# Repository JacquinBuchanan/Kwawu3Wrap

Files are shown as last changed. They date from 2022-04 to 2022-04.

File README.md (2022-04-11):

# Kwawu Arm 3.0 - Wrap Version
This is functional 3D printable device for those with forearm limb differences. It has better functionality and easier to assemble than the 2.0 version.

!!!! DO NOT PRINT THESE STL FILES DIRECTLY. !!!!!
Download all the files and use the OpenSCAD to modify and scale the STL files.

The included PDF file "Kwawu 3.0 Wrap Version Instructional Guide" will show you how to download the Open SCAD program and use the code in these files to size this model.

Instructional videos for this design can be found here.
https://www.youtube.com/playlist?list=PLO2iVws0boe0Yrh_1auXd5TTmXr6_y3zT

I have redesigned the Kwawu arm to be more natural looking and more functional. The terminal device has a much higher grip strength and functionality. Very good at picking up small things with index finger and thumb and big things with whole hand.

This version is the wrap version intended for people with long forearm residual limbs.
There is a socket version for people with short forearm residuals

I would like to thank the e-NABLE community. It is a wonderful group to be a part of.

To get involved with the e-NABLE community please visit https://hub.e-nable.org

Shield: [][cc-by]

This work is licensed under a
[Creative Commons Attribution 4.0 International License][cc-by].

[][cc-by]

[cc-by]: http://creativecommons.org/licenses/by/4.0/
[cc-by-image]: https://i.creativecommons.org/l/by/4.0/88x31.png
[cc-by-shield]: https://img.shields.io/badge/License-CC%20BY%204.0-lightgrey.svg

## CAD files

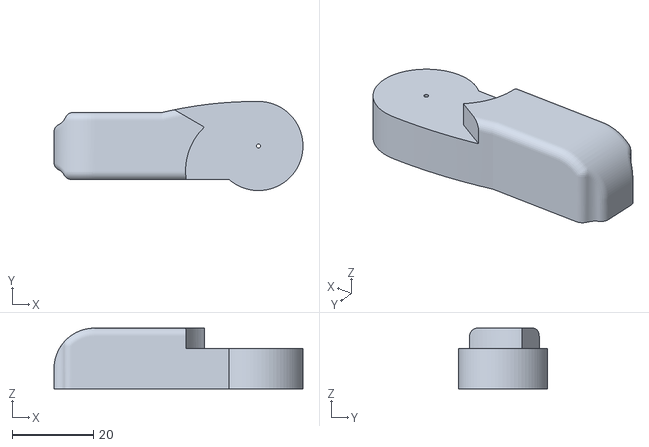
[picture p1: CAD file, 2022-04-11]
o_Arm2.stl
61.4 x 22.0 x 15.0

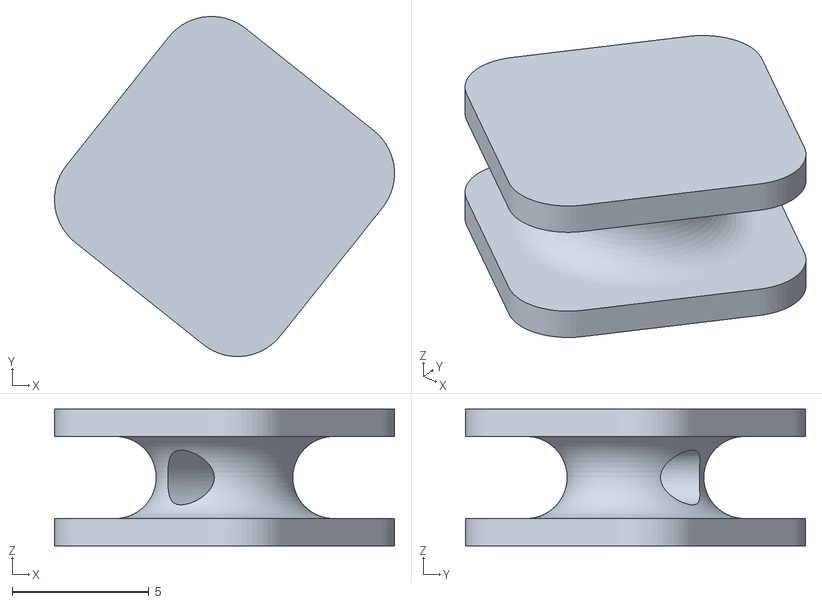
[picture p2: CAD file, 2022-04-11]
o_Tensioner.stl
12.4 x 12.4 x 5.00

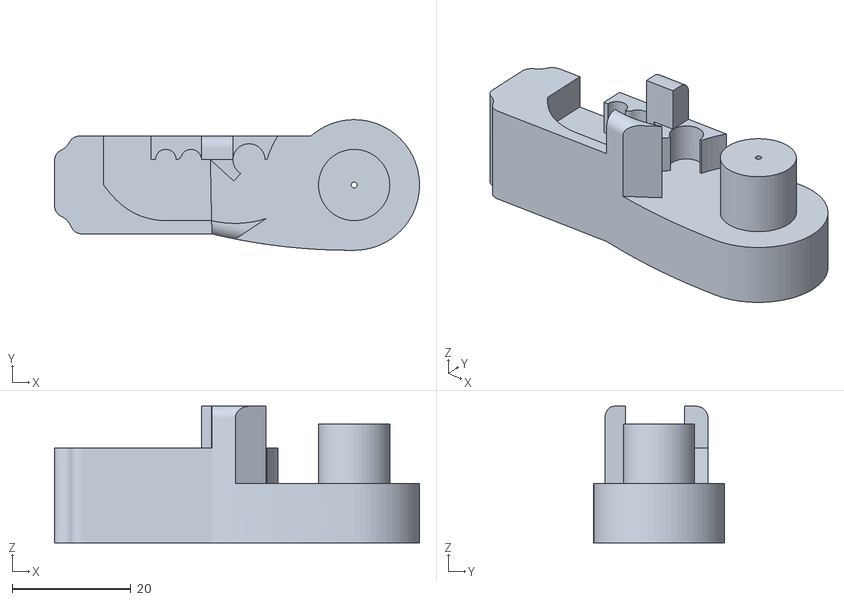
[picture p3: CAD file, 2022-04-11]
o_Arm1.stl
61.4 x 22.0 x 23.0

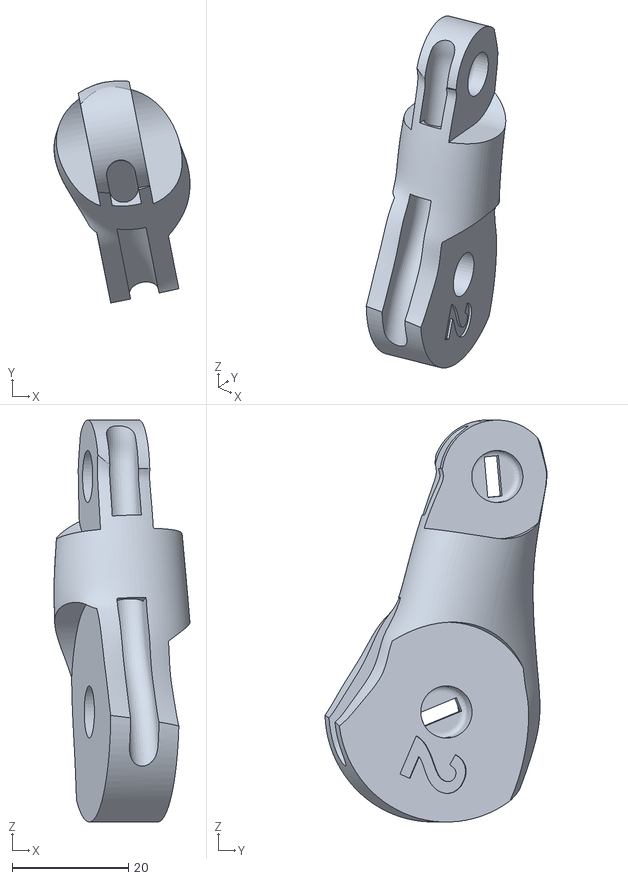
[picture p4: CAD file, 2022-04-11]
o_IndexFingerPhalanx.stl
23.4 x 38.3 x 69.3

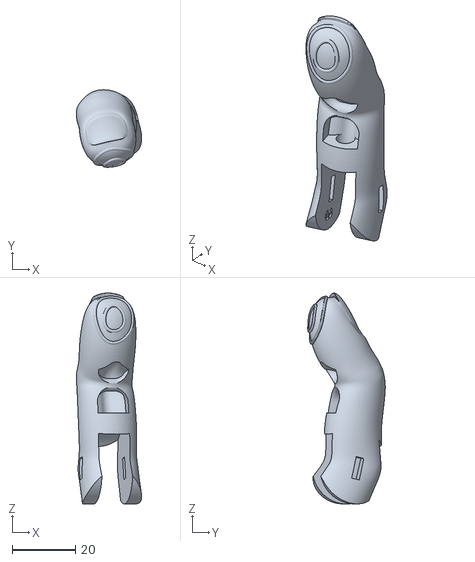
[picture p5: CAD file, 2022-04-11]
o_MiddleFingerEnd.stl
20.6 x 24.5 x 66.6

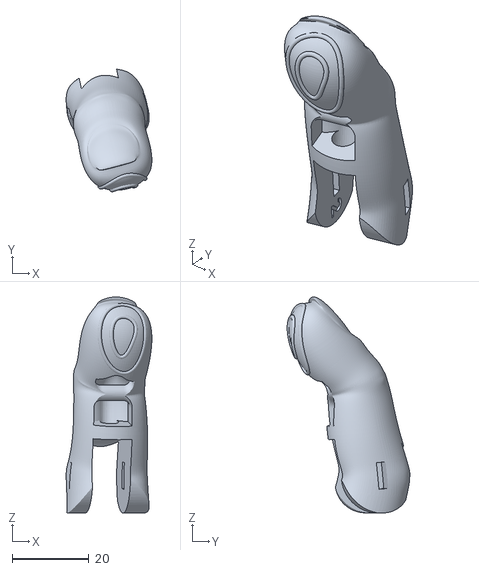
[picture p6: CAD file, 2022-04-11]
o_IndexFingerEnd.stl
22.3 x 31.9 x 56.2

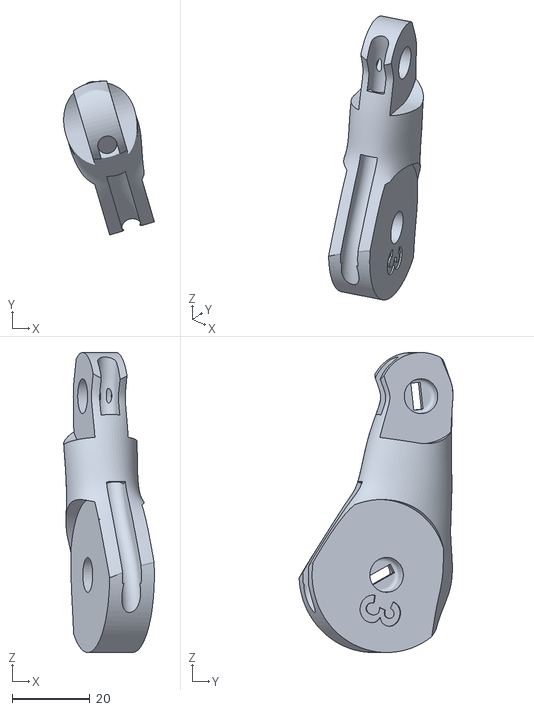
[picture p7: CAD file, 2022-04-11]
o_MiddleFingerPhalanx.stl
23.4 x 39.6 x 77.3

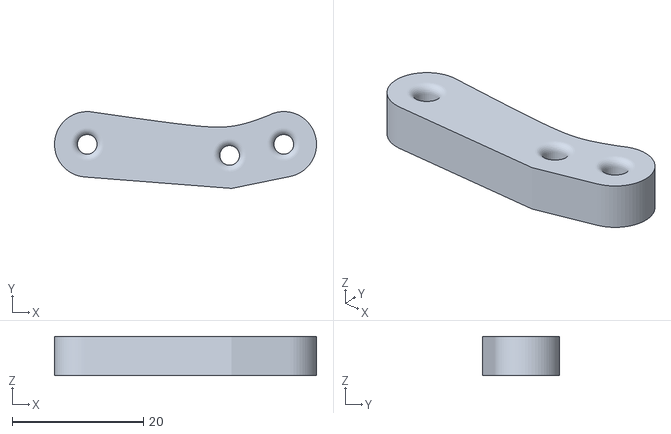
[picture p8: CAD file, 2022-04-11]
o_WhippleTreeSecondary.stl
40.0 x 11.7 x 6.00

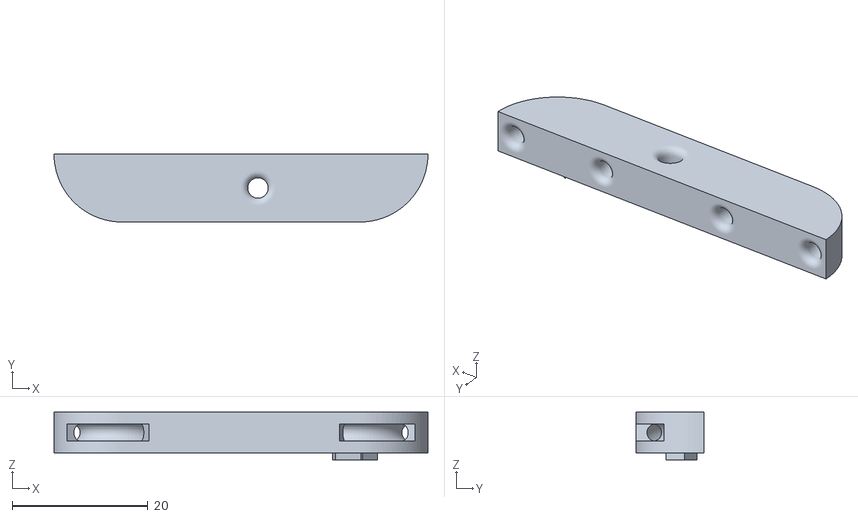
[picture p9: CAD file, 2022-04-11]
o_WhippleTreePrimary.stl
55.0 x 10.0 x 7.00

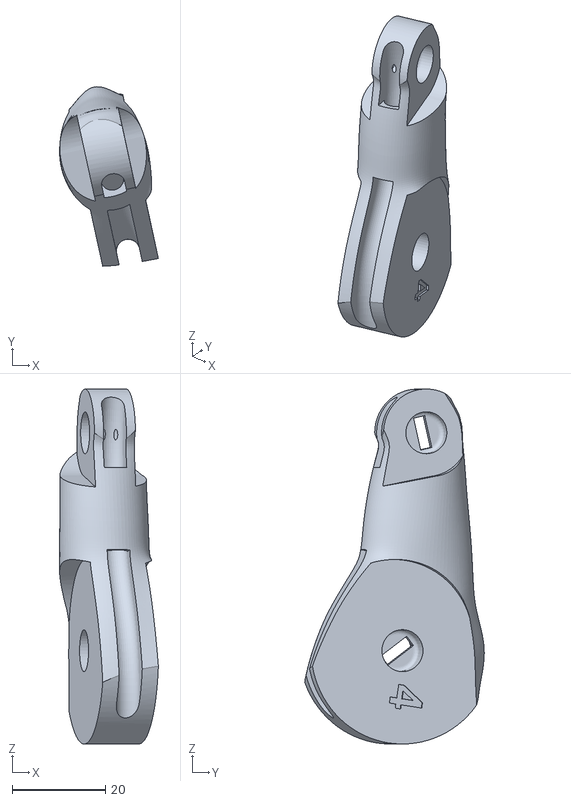
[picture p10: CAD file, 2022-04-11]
o_RingFingerPhalanx.stl
21.1 x 38.5 x 76.1

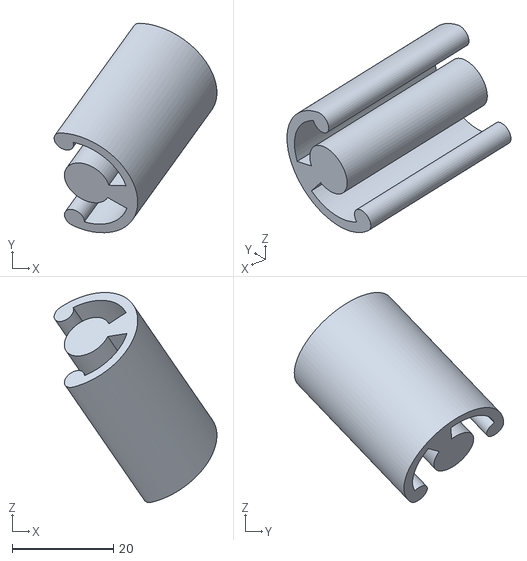
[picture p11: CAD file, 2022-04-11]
o_PencilHolderTool.stl
32.1 x 41.3 x 41.4

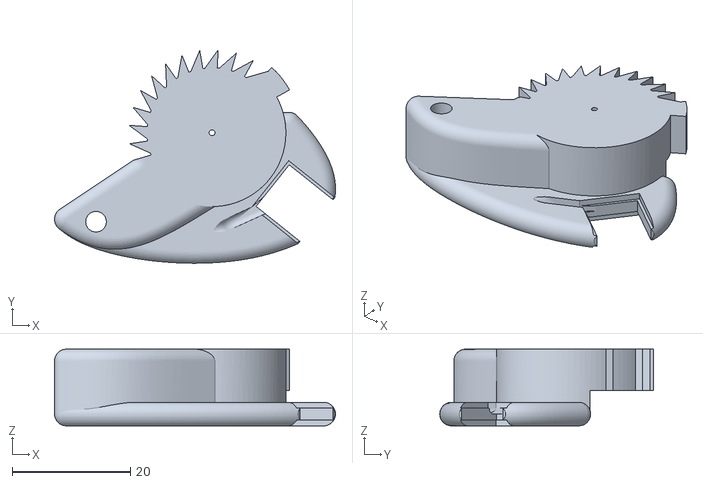
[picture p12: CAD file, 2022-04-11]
o_Ratchet.stl
47.6 x 36.2 x 13.0

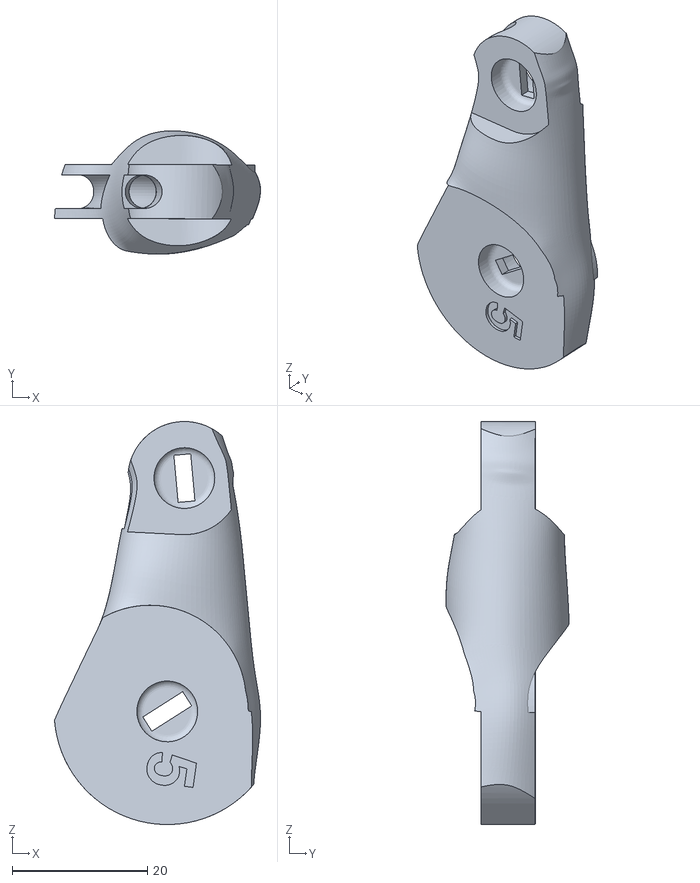
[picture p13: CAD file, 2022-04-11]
o_PinkyFingerPhalanx.stl
30.5 x 18.3 x 59.7

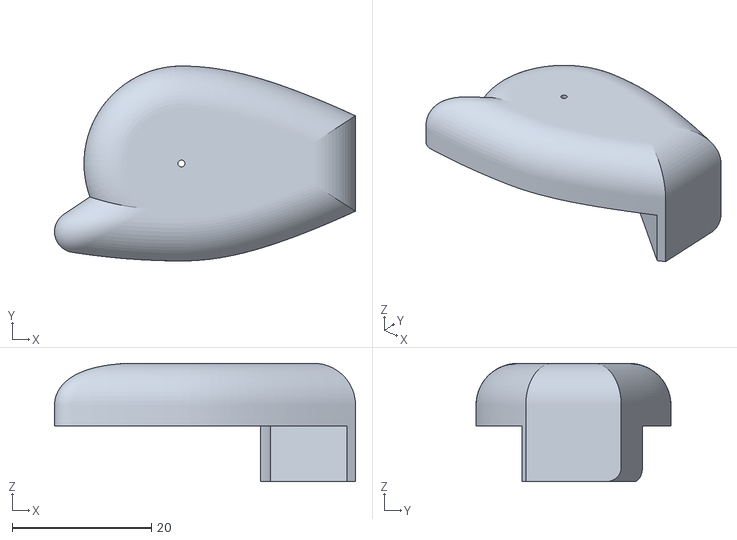
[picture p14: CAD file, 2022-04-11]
o_Cuff1.stl
43.2 x 28.0 x 17.0

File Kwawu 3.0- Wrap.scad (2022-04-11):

// The Kwawu 3.0 prosthetic Arm - Wrap Version
// By Jacqun Buchanan
// Parameteric 3-d printable prosthetic arm
//
// This design is licensed under the Creative Commons - Attribution - Share Alike license.

// The ISO thread code is by Trevor Moseley

// Choose Part
Part = "Cuff1"; // [Palm,PalmTop,WristButton,WristCover, Cuff1,Cuff2,Cuff3,CuffLeatherTemplate,UpperArm1,LowerArm1,UpperArm2,LowerArm2,UpperArm3, LowerArm3, UpperArmLeatherTemplate, LowerArmLeatherTemplate, Ratchet, Latch, LatchCover, WristAttachment, WristBolt, PalmBolt, WristBoltPin, ElbowBolt1,ElbowBolt2,IndexFingerEnd, IndexFingerPhalanx, MiddleFingerEnd, MiddleFingerPhalanx, PinkyFingerEnd, PinkyFingerPhalanx, RingFingerEnd, RingFingerPhalanx, ThumbEnd, ThumbPhalanx, Tensioner, WhippleTreePrimary, WhippleTreeSecondary,PencilHolderCover, Hinges]
//Left or Right Arm
LeftRight = "Right"; //[Right, Left]
//Wraps are made from leather or plastic
LeatherOrPlastic = "Leather"; //[Leather, Plastic]
// Across all four knuckles (mm)
HandWidth = 96; //[65:186]
// Elbow crease to wrist attachment (mm)
ArmLength = 282; //[141: 564]
// Circumference of Forearm just below elbow crease (mm)
ForearmCircumference = 270; //[135: 542]
// - Circumference of Bicep (mm)
BicepCircumference = 294; //[147: 600]
// Padding Thickness -inside forearm and cuff (mm)
PaddingThickness = 2; //[0: 10]
// ISO metric bolt holding palm together (mm) 
PalmBoltDiameter = 6;//[4, 6, 8]
// ISO metric bolt holding cuff and arm together (mm)
ElbowBoltDiameter = 8; //[4, 6, 8, 10, 12, 14]
// Diameter of leather rivet shaft (mm)
RivetShaftDiameter = 5; //[2.4, 2.8, 3.1, 4, 5, 6]
// Velcro strap width (mm)
StrapWidth = 25;//[10: 60]
// Include Pencil Holder
PencilHolder = "No"; // [Yes,No]
/* [Hidden] */


SlotSize = 0.5;
SlotLength = 10;//length of the opening slot
SlotSpacing = 3;//spacing between slots
SlotWidth = 2.4;//width of slots 
//The thickness of the cuff
ShellThickness = 2;

// This is an amount added to the pencil cover length. 
// When this is zero the pencil cover is as tight as possible.
// Make it larger to fit around larger/thicker pencils
PencilCoverAddedLength = 4.0;

PI =  3.141592653589793238;
HandVersion = "V3.0";

HandScale = HandWidth / 96;
WristCircumference = HandScale * 169;
WristCircumferenceWPadding = ((WristCircumference/PI) + 2*PaddingThickness  - 2*ShellThickness)*PI;
ForearmCircumferenceWPadding = ((ForearmCircumference/PI) + 2*PaddingThickness)*PI;
ForeArmCircumferenceScale = ForearmCircumferenceWPadding/270;
ElbowPartsScale = max(0.73, ForeArmCircumferenceScale);
ForearmDiameterWPadding = ForearmCircumferenceWPadding/PI;
BicepCircumferenceWPadding = ((BicepCircumference/PI) + 2*PaddingThickness)*PI;
BicepDiameterWPadding = BicepCircumferenceWPadding/PI;
CuffScale = BicepCircumferenceWPadding/270;
CuffLength = CuffScale * 90;


WristBoltDia = 18;
$fn=30;

if(Part == "Cuff1") {
    if (LeftRight == "Left") {
        mirror([1,0,0]) MakeCuff1();
    }else {
        MakeCuff1();
    }
}

if(Part == "Cuff2") {
    if (LeftRight == "Left") {
        mirror([1,0,0]) MakeCuff2();
    } else {
        MakeCuff2();
    }
}

if(Part == "Cuff3") {
    if (LeftRight == "Left") {
        mirror([1,0,0]) MakeCuff3();
    } else {
        MakeCuff3();
    }
}

if(Part== "CuffLeatherTemplate")
    {
    if (LeftRight == "Left") {
        mirror([1,0,0]) MakeCuffLeatherTemplate();
    } else {
        MakeCuffLeatherTemplate();
    }
}

if(Part == "UpperArm1") {
    if (LeftRight == "Left") {
        mirror([1,0,0]) MakeUpperArm1();
    } else {
         MakeUpperArm1();
    }
}

if(Part == "LowerArm1") {
    if (LeftRight == "Left") {
        mirror([1,0,0]) MakeLowerArm1();
    } else {
        MakeLowerArm1();
    }
}

if(Part == "UpperArm2") {
    if (LeftRight == "Left") {
        mirror([1,0,0]) MakeUpperArm2();
    } else {
        MakeUpperArm2();
    }
}

if(Part == "LowerArm2") {
    if (LeftRight == "Left") {
        mirror([1,0,0]) MakeLowerArm2();
    } else {
        MakeLowerArm2();
    }
}


if(Part == "UpperArm3") {
    if (LeftRight == "Left") {
        mirror([1,0,0]) MakeUpperArm3();
    } else {
        MakeUpperArm3();
    }
}

if(Part == "LowerArm3") {
    if (LeftRight == "Left") {
        mirror([1,0,0]) MakeLowerArm3();
    } else {
        MakeLowerArm3();
    }
}

if(Part == "UpperArmLeatherTemplate") {
    if (LeftRight == "Left") {
        mirror([1,0,0]) MakeUpperArmLeatherTemplate();
    } else {
        MakeUpperArmLeatherTemplate();
    }
}

if(Part == "LowerArmLeatherTemplate") {
    if (LeftRight == "Left") {
        mirror([1,0,0]) MakeLowerArmLeatherTemplate();
    } else {
        MakeLowerArmLeatherTemplate();
    }
}

if(Part == "Ratchet") {
    if (LeftRight == "Left") {
        mirror([1,0,0]) MakeRatchet();
    } else {
        MakeRatchet();
    }
}

if(Part == "Tensioner")
    MakeTensioner();

if(Part == "Latch") {
    if (LeftRight == "Left") {
        mirror([1,0,0]) MakeLatch();
    } else {
        MakeLatch();
    }
}

if(Part == "LatchCover") {
    if (LeftRight == "Left") {
        mirror([1,0,0])  MakeLatchCover();
    } else {
        MakeLatchCover();
    }
}

if(Part == "WristAttachment") {
    if (LeftRight == "Left") {
        mirror([1,0,0]) rotate(a=[180,0,0])MakeWristAttachment();
    } else {
        rotate(a=[180,0,0])MakeWristAttachment();
    }
}

if(Part == "WristBolt") {
    if (LeftRight == "Left") {
        mirror([1,0,0]) rotate(a=[180,0,0])MakeWristBolt();
    } else {
        rotate(a=[180,0,0])MakeWristBolt();
    }
}

if(Part == "WristBoltPin")
{
    rotate(a=[90,0,0])MakeWristBoltPin();
}

if(Part == "ElbowBolt1"){
    if (LeftRight == "Left") {
        mirror([1,0,0]) rotate(a=[180,0,0]) MakeElbowBolt(26);
    } else {
        rotate(a=[180,0,0]) MakeElbowBolt(26);
    }
}

if(Part == "ElbowBolt2"){
    if (LeftRight == "Left") {
        mirror([1,0,0]) rotate(a=[180,0,0]) MakeElbowBolt(19);
    } else {
        rotate(a=[180,0,0]) MakeElbowBolt(19);
    }
}

if(Part == "PalmBolt"){
    if (LeftRight == "Left") {
        mirror([1,0,0]) rotate(a=[180,0,0])MakePalmBolt();
    } else {
        rotate(a=[180,0,0])MakePalmBolt();
    }
}

if (Part == "Palm") {
    if (LeftRight == "Left") {
        mirror([1,0,0]) MakePalm();
    } else {
        MakePalm();
    }
}

if(Part =="WristButton")
{
    //Rotate just to orient for printing
    if (LeftRight == "Left") {
        mirror([1,0,0]) rotate(a=[180,0,0])MakeWristButton();
    } else {
    
        rotate(a=[180,0,0])MakeWristButton();
    }
    
}

if(Part =="WristCover")
{
    MakeWristCover();
    
}

if (Part == "PalmTop") {
    //Rotate just to orient for printing
    if (LeftRight == "Left") {
        mirror([1,0,0]) rotate(a=[90,7,]) MakePalmTop();
    } else {
        rotate(a=[90,7,0])MakePalmTop();
    }
}

if(Part == "IndexFingerEnd") {  
    if (LeftRight == "Left") {
        mirror([1,0,0]) IndexFingerEnd();
       } else {
        IndexFingerEnd();
    }
}

if(Part == "IndexFingerPhalanx") { 
     if (LeftRight == "Left") {
        mirror([1,0,0]) IndexFingerPhalanx();
       } else {
        IndexFingerPhalanx();
    }
}
        
if(Part == "MiddleFingerEnd") { 
     if (LeftRight == "Left") {
        mirror([1,0,0]) MiddleFingerEnd();
       } else {
        MiddleFingerEnd();
    }
}
            
if(Part == "MiddleFingerPhalanx") { 
     if (LeftRight == "Left") {
        mirror([1,0,0]) MiddleFingerPhalanx();
       } else {
        MiddleFingerPhalanx();
    }
}
                
if(Part == "PinkyFingerEnd") { 
     if (LeftRight == "Left") {
        mirror([1,0,0]) PinkyFingerEnd();
       } else {
        PinkyFingerEnd();
    }
}

if(Part == "PinkyFingerPhalanx") { 
     if (LeftRight == "Left") {
        mirror([1,0,0]) PinkyFingerPhalanx();
       } else {
        PinkyFingerPhalanx();
    }
}

if(Part == "RingFingerEnd") { 
     if (LeftRight == "Left") {
        mirror([1,0,0]) RingFingerEnd();
       } else {
        RingFingerEnd();
    }
}

if(Part == "RingFingerPhalanx") { 
     if (LeftRight == "Left") {
        mirror([1,0,0]) RingFingerPhalanx();
       } else {
        RingFingerPhalanx();
    }
}

if(Part == "ThumbEnd") { 
     if (LeftRight == "Left") {
        mirror([1,0,0]) ThumbEnd();
       } else {
        ThumbEnd();
    }
}

if(Part == "ThumbPhalanx") { 
     if (LeftRight == "Left") {
        mirror([1,0,0]) ThumbPhalanx();
       } else {
        ThumbPhalanx();
    }
}

if(Part == "WhippleTreePrimary") { 
     if (LeftRight == "Left") {
        mirror([1,0,0]) rotate(a=[180,0,0])WhippleTreePrimary();
       } else {
        rotate(a=[180,0,0])WhippleTreePrimary();
    }
}

if(Part == "WhippleTreeSecondary") { 
     if (LeftRight == "Left") {
        mirror([1,0,0]) WhippleTreeSecondary();
       } else {
        WhippleTreeSecondary();
    }
}

if(Part == "PencilHolderCover")
{
    PencilHolderCover();
}
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

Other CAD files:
o_ThumbEnd.stl
o_ThumbPhalanx.stl
o_LatchCover.stl
o_Palm.stl
Arm1.stl
o_Cuff2.stl
o_Latch.stl
o_PalmTop.stl
o_PinkyFingerEnd.stl
o_RingFingerEnd.stl

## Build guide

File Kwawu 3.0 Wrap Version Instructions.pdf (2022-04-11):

# Kwawu Arm 3.0 Wrap Version

# Instruction Guide

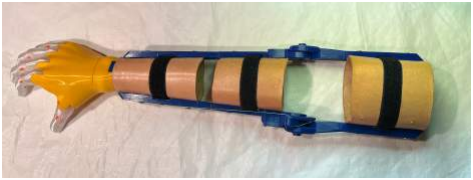
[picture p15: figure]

# Jacquin Buchanan January 2022

This work is licensed under the Creative Commons Attribution 4.0 International License. To view a copy of this license, visit https://creativecommons.org/licenses/by/4.0/ or send a letter to Creative Commons, PO Box 1866, Mountain View, CA 94042, USA.

In simple language you can:
- Share — copy and redistribute the material in any medium or format.
- Adapt — remix, transform, and build upon the material for any purpose, even commercially.
Under the following terms:
- Attribution — You must give appropriate credit, provide a link to the license, and indicate if changes were made. You may do so in any reasonable manner, but not in any way that suggests the licensor endorses you or your use.
- No additional restrictions — You may not apply legal terms or technological measures that legally restrict others from doing anything the license permits.

Kwawu Arm 3.0 Wrap Version 2

This instruction guide shows the steps and processes in making a Kwawu 3.0 transradial prosthetic arm and hand. This arm is best suited for a recipient with a residual forearm longer than half of the recipient’s intact forearm. See the Socket version of the Kwawu 3.0 for an arm better suited for a residual arm that is half or shorter than the recipient’s intact arm.

To complete the instructions in this document and fully prepare an arm for usage can take 30 to 40 hours of labor. Assuming most people reading this document are doing this project in their spare time, expect it to take several weeks. Likely the first one you make may not fit or work exactly right, when you try it on the recipient, so you will have to reprint a part and partially reassemble the arm. It is important to set this expectation for yourself and the person you are making the arm for. Explain to them and yourself that the whole process can take months.

Improvements of the Kwawu 3.0 over the Kwawu 2.0 device include:

- Easier stringing the fingers to hand mechanism
- Better response of elbow bend to finger squeeze
- A locking but adjustable wrist
- Improved latch mechanism to fix hand fingers in a grasped position
- The Cuff and Forearm have plastic or leather options
- Thermoforming is not required
- A redesigned tensioner
- Easier assembly
- Compatible with wider range of TPU ShoreA hardness

# Qualifying Expectations

This arm was designed by hobbyists in hopes that it would fill a need for someone who has had a congenital or traumatic amputation. We do not claim to be professional prosthetists and this arm is designed as an assistive device not a custom prosthetic. This was designed to be used as an assist in everyday functional activities. These are step by step instructions for fabrication of the arm. Our team is available to help problem solve and answer questions should you have difficulties. If you are in need of this assistive device but are unable to make it or have it made we are happy to assist with that as well. As hobbyists our goal is to help make an assistive device which makes day to day activities a little easier.

## This Process of making a Kwawu 3.0 Wrap Version is described in the document and is divided into 3 sections, namely:

Section 1: Preparing Files for Printing.

## Section 2: 3D Printing of the Necessary Parts

## Section 3: Assembly of the Kwawu Arm 3.0 Wrap Version

# Section 1: Preparing files for printing

## Overview

1. Download the Kwawu 3.0 Wrap version from www.thingiverse.com. (http://www.thingivers.com) DO NOT print the stl files directly—they will not result in a functional device—files must be translated into usable stl files using the customizer in OpenSCAD.
2. Download the latest version of OpenSCAD from http://openscad.org/downloads.html Then open the file “Kwawu 3.0- Wrap.scad.
3. Obtain required measurements from the recipient — Record values for the recipient in Table 1.
4. Fill in the OpenSCAD parameters with the specific values of the recipient’s measurements.
5. Render all appropriate parts in the display and save the result as a file.

## Download Kwawu 3.0 files

When you download the files from thingiverse there is one .scad file and a bunch of .STL files. DO NOT print the STL files directly. The Open SCAD software will load the STLs and “modify “ them to fit the recipient.

## Download and Install OpenSCAD

1. Download the latest version of OpenSCAD. http://openscad.org/downloads.html
2. Once you have installed OpenSCAD, click on “New” then in the top menu, select File>Open. Browse and click on the file “Kwawu 3.0- Wrap.scad ''
3. Uncheck ‘Hide Customizer’ in the View menu (as shown below) to show the Customizer UI at the right.

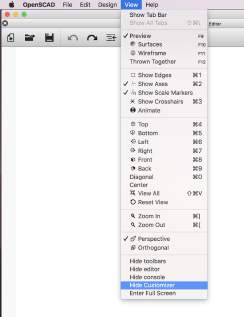
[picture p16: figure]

4. In the Customizer menu on the Right Hand side, click the little black arrow to display the parameters. Make sure “Automatic Preview” and “Show Details” are both checked.

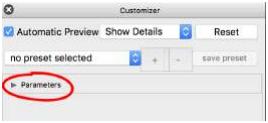
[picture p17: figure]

5. Hit the Preview button (F5) to get a quick preview (should not be necessary if ‘Automatic preview’ is enabled).
6. You should see a preview of the Cuff1 in the main window. It looks something like this.

7. If the object is too large or small press the “View all” button

The view will change to something like this.

Now you are ready to set all the sizing parameters. Once you have set all the parameters you will need to render each part and save to an STL file.

## Measuring Your Recipient

There are several measurements you will need from the recipient. The circumference measurements you will want to make on the residual arm. The Forearm Length and Hand Width you will make on the intact arm. All measurements are in millimeters.

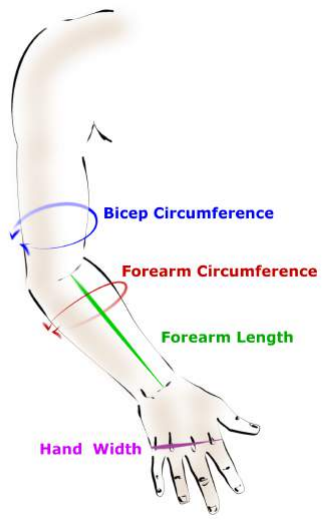
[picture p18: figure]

Measurements Diagram
Bicep Circumference: Measured around the upper arm at its thickest point. Measured on the residual arm being fitted with the prosthesis.

Forearm Circumferences: This is a series of measurements meant to capture the shape of the forearm socket. Starting at the recipient’s residual elbow crease, measure the forearm’s circumference.

Forearm Length : This is measured from the elbow crease to the wrist crease on the recipient's intact arm. Instead of inputting this value as the Forearm Length, we recommend a length a few centimeters longer than the residual arm (leaving enough space for the wrist mechanism). A shorter arm length is easier for maneuverability and better mechanical advantage. This “Kwawu 3.0 Wrap” design is intended for recipients with residual arms almost as long as the intact arm.

Hand Width: Measured on the intact arm. The measurement is across the knuckles in millimeters.

## Fill in the OpenSCAD Parameters

Once you have measurements from the recipient you will enter various parameters into the Customizer Parameters side bar.

An example of an OpenSCAD Parameters section is shown below. Note that besides the measurements from the recipient, there are other choices to be made as well. These are also described subsequently.

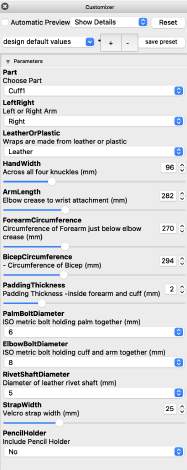
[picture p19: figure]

In OpenSCAD, it may be easier to turn OFF Automatic Preview while entering parameters. Many of these parts are slow to render so having the preview run while entering numbers can make the user interface cumbersome.

Detailed information on choices is necessary to render parts to make printable stl files. All 3D parts to be printed must be rendered using the selected choices matching the recipient’s measurements and/or preferences. A description of these choices are listed below in order. Table 1 shows the acceptable ranges of these choices and allows you to fill in specific values for your recipient

OpenSCAD Parameters

Parameter Name | Description
Part | These include all parts necessary to assemble a Kwawu3 wrap Arm. Choose each of the 40 parts, one by one, then render and save each one. Before rendering any parts, be sure all the other parameters are set to match the recipient. Input or use the sliders to set the values. Uncheck “Automatic Preview” if you have issues with inputting values. After rendering, go to File>Export>As STL . Name the file to correspond to the part rendered and Save. See “Leather or Plastic” for an exception in the export file choice.
Left or Right Arm | The side of the body for the prosthetic arm required by the recipient.
LeatherOrPlastic | This option offers the maker to select all leather or all plastic forearms and cuffs. Leather may be a more comfortable option over the plastic version. If the Leather option is chosen, then all templates must be rendered but saved as an SVG file. To do this go to File>Export>Export as SVG. Name the file compatible with the template such as “CuffLeatherTemplate” and save. For the leather option Cuff3, UpperArm3 and LowerArm3 will not render as they are not needed in the leather option
Handwidth | Measure the width of the recipient’s intact hand at the knuckles.
ArmLength | Arm length is typically chosen based on the recipient’s “good” arm—or it may be purposely made shorter for easier maneuverability and better mechanical advantages, but make sure to choose a value longer than the recipient’s residual. The Wrap version is primarily meant for recipients with a residual longer than half the recipient’s intact arm.
Forearm Circumference | Measure the circumference of the forearm just below the elbow crease.
Bicep Circumference | Measure the circumference of the bicep where the cuff will wrap around.
Padding Thickness | Padding is not recommended for the leather version. For the plastic version, padding is recommended to be inserted in the upper arm area where the recipient’s forearm residual and bicep area will contact the prosthetic. The more comfortable option is silicone sheeting —e.g.

https://amputeestore.com/products/silipos-pressure-relief-gel-padding?variant=41 14763009 (https://amputeestore.com/products/silipos-pressure-relief-gel-padding?variant=4114763009) — but the more expensive option.

| Closed cell neoprene is a less expensive but still a good option. Here are links to a couple of these: https://www.amazon.com/Insulation-Neoprene-Adhesive-Multi-Function-Soundproof/dp/B08R9LF7BX (https://www.amazon.com/Insulation-Neoprene-Adhesive-Multi-Function-Soundproof/dp/B08R9LF7BX) https://www.amazon.com/NATGAI-Neoprene-Adhesive-Multiple-Dimensions/dp/B0 7VY7SFRP (https://www.amazon.com/NATGAI-Neoprene-Adhesive-Multiple-Dimensions/dp/B07VY7SFRP) 2mm is the typical thickness for padding.
PalmBolt Diameter | Bolts for the palm can be printed, however, we recommend small bolt sizes (diameter 4mm or less) should be purchased as metal or nylon bolts to reduce the chance of bolt breakage. Also, we recommend the sizes chosen to be in proportion to the arm size, i.e. use small bolts for a small arm and a larger one for larger arms.
ElbowBolt Diameter | Bolts for the elbow can also be printed, however, we recommend small bolt sizes (diameter 4mm or less) should be purchased as metal or nylon bolts to reduce the chance of bolt breakage. Also we recommend the sizes chosen to be in proportion to the arm size, i.e. use small bolts for a small arm and larger one for larger arms.
RivetShaft Diameter | Rivet shaft diameter only applies to the leather version and to how large the holes should be in Cuff 1 and Cuff 2 as well as Arm1 and Arm2 parts. Rivet shafts come in different sizes. An alternative to rivets are Chicago screw/post sets.
StrapWidth | Velcro Straps are required on the Cuffs and Forearms for both the leather and plastic versions. Strap widths of 25 mm are typically used for larger sized arms and 10mm for small sizes.
PencilHolder | A Pencil holder on the palm is an option and should be made with TPU.

(Paragraph deleted–redundant)

Table 1: OpenSCAD Options and Ranges (see note 1)
Parameter Range | units | Recipient Values

Part | See separate list | | n/a
Left or Right | Left or right
Leather or Plastic | Leather of Plastic
Handwidth | 65 - 186 | mm
ArmLength | 141-564 | mm
ForearmCircumference | 135-542 | mm
BicepCircumference | 147-600 | mm
PaddingThickness | 0-10 | mm
PalmBoltDiameter | 4, 6, or 8 | mm
ElbowBoltDiameter | 4, 6, 8, 10, 12 or 14 | mm
RivetShaftDiameter | 2.4, 2.8, 3.1, 4, 5, or 6 | mm
StrapWidth | 10-60 | mm
PencilHolder | yes or no

## Render all appropriate parts

Select each part in the Parts dropdown.Then Press Render.

NOTE: The render button can take a long time for some parts (20 minutes or more).

Save STL (exception—leather template). Export and save the stl files under a name that identifies each part. For the CuffLeatherTemplate choose FILE->EXPORT->EXPORT As SVG

# Section 2: 3D Printing of Necessary Parts

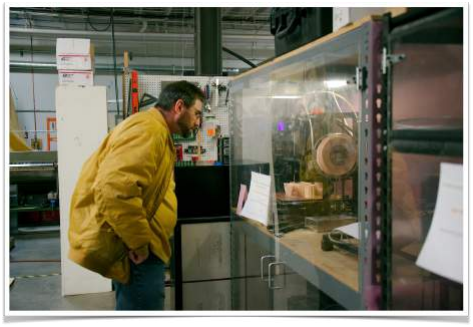
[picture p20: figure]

Table 2 shows all parts available for printing along with quantity required, material typically used, and if supports (bed contact) are generally used. PETG is the material recommended for most of the parts because of its strength and solvent resistance—other materials may be tried but we cannot predict a good outcome. Use a suitable TPU for hinges and pencil the holder.

Printing Recommendations

Typical print temperature and print speed recommended for the material (PETG or TPU).

Infil should be 35% and of honeycomb geometry.

If you are using a printer with a 0.5mm nozzle, you may find a linewidth of 0.4mm works better for some parts (e.g. latch).

We recommend the number of top and bottom layers to be 10 layers. The reason is that the 2mm flexible plastic grid in the case of the plastic cuff has been engineered for flexibility and strength as a solid device. If 10 layers for both and bottom layers are used, we can be certain the grid will be solid but changes won’t be necessary for other parts. Make sure the gaps in the grid are open—if not you may need to raise the z height so the bottom layer/layers will not be spread out which could cause gaps to be fused closed. If gaps are closed, the grid may be inflexible.

### Note: All the parts are rendered from OpenSCAD in the orientation we think is best for printing. Though, you may need to adjust the orientation based on

your particular printer.

A brim is recommended for the finger ends and phalanxes to enhance part stability during printing.

Printing the finger pieces can also benefit from
supports/scaffolding. Generally it is better to use a slicing program that will let you manually place the scaffolding for these parts. If you are having trouble with the fingers coming loose from the base plate, try learning them back to a 45 degree angle and adding more scaffolding. This may add to the time to clean the parts, but can be more reliable for some printers.

### Note: If scaffolding is used, it is better to be manually added than be auto-generated by the printing software. Auto-generated scaffolding can

block holes and make it very difficult to string the hand.

### Make sure to review the scaffolding so it DOES NOT get created inside a channel or hole where it can be very difficult to remove

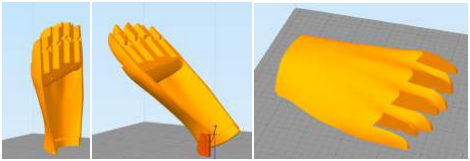
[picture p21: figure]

Three orientations to print the Palm Top. The 45 degree angle was suggested by Krzysztof Grandys and is my preferred orientation for best look and strength.

If the leather option was chosen, open the SVG files (saved in the OpenSCAD procedure) in your browser. We have found the Chrome browser opens with an accurate size representation so that you can simply print out the template on paper. We have also used Safari to open the SVG file but found it necessary to size the printing to match the holes in the Cuff, UpperArm and LowerArm prints. Once an accurate template is printed, lay it out on the leather and cut the outline. Plan to use the smoothest side of the leather in contact with the recipient’s skin for greater comfort. A leather punch is recommended to make accurate holes in the leather where it will attach to the plastic components. We also recommend ~4.5 oz leather (~1.8mm thick). It is the more expensive option but we believe it to be more comfortable than the plastic. A website of one supplier of cowhide leather is www.montanaleather.com

One choice that is not required in the OpenSCAD options is arm color. The recipient should be consulted about their choice in color for their arm so the printer can purchase a filament color as close as possible to the recipient’s choice. If a suitable color is not found, it is possible to use spray paint to better match the recipient’s choice. The arm may also be decorated according to the recipient’s wishes.

Total printing time for all parts may be 30 to 40 hours. After each print, remove any support structures and sand or file any rough edges or corners. Additional sanding or filing may be necessary when fitting parts together during assembly. Printing several small parts in the same print job will cut down on total print time.

TPU is required for hinges and the pencil holder. Hinges have been design engineered to use a TPU of Shore A hardness range of 85A to 95A . ShoreA hardness 85A is preferred but more difficult to print than 95A. The brand NinjaFlex is the original material from a company called NinjaTek. They have since come out with several other flexible filaments all with different

properties, so be sure to get the one with Shore A Hardness of 85A.

### Likewise, FilaFlex is a company whose original product was Shore Hardness 82A. They have since come out with FilaFlex Medium which is Shore A Hardness 95A. Shore A Hardness 95A will work for Kwawu 3.0 hinges but since it is stiffer than ShoreA hardness of lesser values, it would be less

responsive.

### For hinges, make sure the printed parts fit into their appropriate slots snuggly, i.e. will not fall out and will fit into the slots without trimming. Since printers can vary, it may be necessary to scale the print in your slicer to

obtain a proper fit.

Table 2: Printing the Parts

Parts | Quantity | Material | Supports
Palm | 1 | PETG | yes
PalmTop | 1 | PETG | optional
WristButton | 1 | PETG | no
WristCover | 1 | PETG | no
Cuff1 | 1 | PETG | yes
Cuff2 | 1 | PETG | yes
Cuff3 | 0 or 1 | PETG | no
CuffLeatherTemplate | 0 or 1 | | n/a
UpperArm1 | 1 | PETG | optional
LowerArm1 | 1 | PETG | no
UpperArm2 | 1 | PETG | no
LowerArm2 | 1 | PETG | no
UpperArm3 | 1 | PETG | no
LowerArm3 | 1 | PETG | no
UpperArmLeatherTemplate | 0 or 1 | | n/a
LowerArmLeatherTemplate | 0 or 1 | | n/a
Ratchet | 1 | PETG | yes
Latch | 1 | PETG | no
LatchCover | 1 | PETG | no
WristAttachment | 1 | PETG | no
WristBolt | 1 | PETG | no
PalmBolt | 0 or 2 | PETG/ metal/nylon | no
WristBoltPin | 1 | PETG
ElbowBolt1 | 0 or 1 | PETG/ metal/nylon | no
ElbowBolt2 | 0 or 1 | PETG/ metal/nylon | no
IndexFingerEnd | 1 | PETG | optional
IndexFingerPhalanx | 1 | PETG | optional
MiddleFingerEnd | 1 | PETG | optional
MiddleFingerPhalanx | 1 | PETG | optional

PinkyFIngerEnd | 1 | PETG | optional
PinkyFingerPhalanx | 1 | PETG | optional
RingFingerEnd | 1 | PETG | optional
RingFIngerPhalanx | 1 | PETG | optional
ThumbEnd | 1 | PETG | optional
ThumbPhalanx | 1 | PETG | optional
Tensioner | 1 | PETG | no
WhippleTreePrimary | 1 | PETG | no
WhippleTreeSecondary | 1 | PETG | no
PencilHolder | 0 or 1 | TPU | no
Hinges | 1 set | TPU | no

# Section 3: Kwawu 3 Assembly-Wrap Version

## How does the Arm Work?

Familiarize yourself with the function of the arm prior to building. The fingers are supposed to close with the thumb first and the pinky last. When the fingers close in order, you get the precision of the thumb and index finger first, while the remaining fingers are still out of the way. This enables you to pinch or to pick up finer objects. If you continue to close the grip the other fingers engage as would happen around a bottle or baseball.

The wrist button allows the wrist to freely rotate when pressed and “lock” in place when released. Different wrist positions are useful for different applications.

The latch allows the grip to stay closed tight with the elbow moving freely. With the latch open, the grip opens and closes with the elbow movement. With the latch closed, the string is held as the elbow closes. This allows the user to hold a grip while still using the elbow motion. An example where the latch is useful is when the user needs to hold a spoon while eating or a grabber bag while walking. Move the latch slider back to the open position to release the grip.

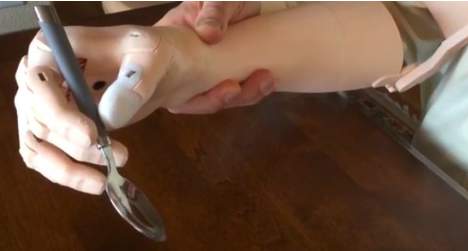
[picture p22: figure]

Note: Assembly videos have been prepared and are supplemental or maybe used in place of this document. See at www.onemonkclapping.com

Phase 1 : Preparation
- Gather Materials
- Identify and Arrange Parts
- Prepare the Printed Parts Phase 2 : Hand
- Assembling the Hand
- Stringing the Hand
- Tensioning
Phase 3: Forearm
- Assembling the Forearm
- Assemble the Cuff
Phase 4: Putting it all together
- Attaching Hand to Arm
- Assembling the Latch
- Final Tensioning and Knotting Phase 5: Final Tests and Fitting
- Straps, Finger Tips, and Palm Grip
- Padding and Fitting

## Gather Materials Tools needed for Assembly

We tried to keep the required tools list as short as possible.

Thick CA glue such as Super Glue for sealing the knots in the fishing line and for assembling the forearm.

Two part epoxy is better to assemble arm pieces, if you print the arm in two pieces.

Phillips head screwdriver to fit the Sheet metal screws (#4 pan head)

Hexagonal allen wrench or Robertson square head drive. Depends if you use metal purchased bolts or the 3d printed bolts.

Sharp knife or scissors to cut the fishing line.

## Tools Recommended for Assembly

These tools will make your assembly easier and generally result in a better device.

Small flat file , Small round file , Medium half round file sanding blocks or sandpaper to clean printed parts.

Toothpick or similar disposable fine tip to help spread the glue.

Utility knife or razor to help clean parts. A sharp razor is helpful to clean “stringing” off the flexible parts and is very useful to trim the hinges.

A pair of needle nose pliers can come in handy, particularly when removing scaffolding.

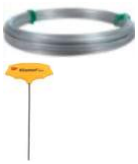
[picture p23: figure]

Galvanized Picture Hanging Wire and/or a T handle Ball End Allen Wrench
Both are very useful in clearing the string holes in the fingers and palm if they close up during 3-D printing. The wire helps pass the string in difficult places. Galvanized wire comes in many sizes at the local hardware store. It is generally stiff enough to force through the holes to open them up.

Plasti Dip - clear
We paint this on the fingertips and the entire palm grip area. This creates a much better grip, than the plastic by itself. It is durable when used with the primer.

A thread Tap tool is handy. You can always heat a metal bolt and use it to clean the threads in the plastic but a tapping tool is made to do this and would do a better job. You likely will only need a few sizes which correspond to the size of your palm and elbow bolts.

## Parts and Supplies

These are the materials you will use for each build.

Dyneema fishing line—80 to 120 test strength Dyneema is the name of material used in recommended fishing line. For a 100% size hand you will need about 10 feet. Purchase extra to allow for adjustments in tensioning and restringing of the hand. (e.g. brand names include Spiderwire or Hercules).

Steel rod of 2mm diameter.
2mm rods are available on Amazon. https://www.amazon.com/gp/product/B07D2WSF29
Typical wire clothes hangers are suitable or hardware stores sell this diameter steel.
To stabilize the latch mechanism you only need a short piece. To strengthen the forearm you will need four pieces about 100mm each.

Self Adhesive Padding in areas intended to be in contact with the recipient’s skin (cuff and forearm) is recommended. The thickness of this padding should have already been designated in the OpenSCAD “padding thickness” choice section. If the leather option is chosen, no padding is needed.
Silicone: https://amputeestore.com/products/silipos-pressure-relief-gel-padding Neoprene:
https://www.amazon.com/Insulation-Neoprene-Adhesive-Multi-Function-Soundproof/dp/B08R9LF7BX
or
Neoprene:
https://www.amazon.com/NATGAI-Neoprene-Adhesive-Multiple-Dimensions/dp/

B07VY7SFRP

Velcro Straps —the width of these straps should have been already designated in the OpenSCAD “StrapWidth” choice option. Generally, 8” to 12” long, 1” wide, non-elastic (often sold as cable straps). For small arms you can use 1/2” wide

Palm bolts Cap Head It is recommended to use store bought nylon bolts because they are lighter than metal bolts and more durable than the 3-D printed ones.
The bolts need to match the thread size specified in the OpenSCAD. Most hardware stores will carry these bolts.

Elbow Bolts round head - A nice smooth round head store bought nylon bolt is the best option. When printing with PETG I have had good luck with the printed elbow bolts. But they can break while tightening which can be frustrating to get cleared out.
The bolts need to match the thread size specified in the OpenSCAD. Most hardware stores will carry these bolts.

Sheet metal screws (#4 pan head) of appropriate length for attaching socket wrist to Palm (1 ea.) and for attaching LatchCover to Upper Arm (1 ea.) The #4 size is US standard, outside the US it is a 3mm sheet metal screw.

ThreadLocker Blue Gel
Once you have assembled everything, it is recommended to put on the bolt threads so they do not work loose. You can use glue if you do not have this.

Rivets and/or Chicago screw/post Applicable to the leather option only. For smaller sizes, we prefer copper rivets. They are small and can be cut to length. The down side is you can crush the plastic if you are not careful. https://www.amazon.com/gp/product/B08HMYMFWS
For larger sizes we prefer Chicago screws. They are reusable, but only come in a limited number of lengths and diameters.
Make sure the correct diameter of the shaft is set in the OpenSCAD options

Leather We recommend ~4.5 oz leather (~1.8mm thick). It is the more expensive option compared to plastic, but we believe it to be more comfortable than the plastic. You can print the leather template SVG files on paper, and use that to determine how much leather you will need.
A leather punch is recommended to make accurate holes in the leather where it will attach to the plastic components. A website of one supplier of cowhide leather is www.montanaleather.com

### To determine which size and length to purchase for the elbow and palm bolts, use the 3-D printed bolts and the parameters on OpenSCAD. It is

helpful to bring the sample 3-D printed bolts with you to the store.

### Both metal and nylon bolts can be cut if they are too long and if you have the

proper tools.

## Identify and Arrange Parts

## Identify the correct parts for the fingers and palm and

arrange them in order.

## The finger pieces have

numbers embossed in them.

## These correspond to the finger numbers 1 to 5 starting

with the thumb.

## The location of the number on the fingers will verify that you

have a Right or Left Hand.

## Prepare the Printed Parts

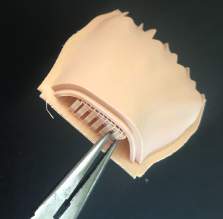
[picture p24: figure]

# Thoroughly Remove the Scaffolding

## This is an important step. Make sure you remove all scaffolding in

the corners and edges.

# Sand, File and Smooth Parts

## Sand, file and generally finish the parts. If you oriented the finger phalanx as suggested during the printing process, you will need to sand the curved back end of the parts. The added supports and spreading will mean the back is not

round.

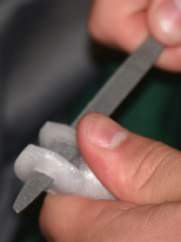
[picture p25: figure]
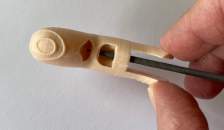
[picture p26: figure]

## Clean string channels

## In smaller printed hands the holes for the strings can close during the printing process. Galvanized picture wire is generally stiff enough to force through the holes to open

them up.

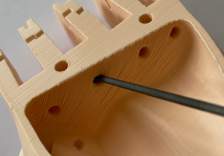
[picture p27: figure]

## You can also force the wire through the opening, heat it with a solder iron, and move it around to smooth

the inside of the channels.

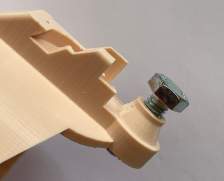
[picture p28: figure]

## Clean the Palm and Elbow threads Using a metal bolt or a tap tool,try screwing the bolts into just the threaded part. The top of the palmtop and the elbow have threads matching what was set by

OpenSCAD.

## You may need to heat the bolt to

help clean the plastic threads.

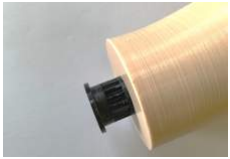
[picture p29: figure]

## Clean the wrist bolt threads Try screwing the wrist bolt in the forearm. Make sure it is smooth and

easy to tighten all the way.

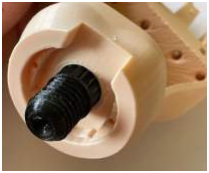
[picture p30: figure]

## Clean wrist button mechanism The wrist button is printed with very tight tolerances. You will likely need to sand the ratcheting part of the

wrist bolt to a smooth round finish.

## Insert the wrist bolt from the inside of the palm. Make sure it rotates easily, yet is sung

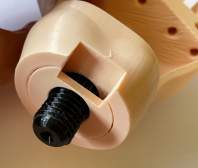
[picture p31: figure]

## Put the Wrist cover over the wrist bolt, WITHOUT the WRIST BUTTON. Make sure the wrist bolt can rotate smoothly and easily yet

does not rattle.

## Take the wrist bolt back out after

the test.

B. Hand Assembly
1. Gather all parts of the hand together. Each finger end and phalanx has a number that is imprinted on it, i.e. 1=thumb, 2=index, 3=middle, 4=ring, and 5=pinky. Fit the pieces together —all should fit and move without undo friction that might impede bending. It may be necessary to use a file, utility knife, or sandpaper to facilitate finger movement. The rectangular holes should also be free of burrs or print filament webbing.
2. Insert the TPU hinges in the slots between the finger ends and the finger phalanxes. Insert other TPU hinges in the phalanx top and slide the ends into the slots in the palm.
3. Stringing the hand is fairly straightforward and much easier than previous Kwawu versions. Figure 1 shows the fingers and the stringing route. Figure 1 along with Figure 2 show a right hand strung appropriately. A left hand (not shown) would be the mirror image of these figures.

4. There is a structure at the end of each finger for tying a knot. Use Super glue to fix the knots from slipping. Note that the long end of the secondary whippletree is toward the thumb and String 1 from the thumb connects to it (Figure 2). String 2 connects index finger end to middle finger end via the thumb end of the primary whippletree. Note the imprinted arrow on the primary whippletree will point toward the thumb. String 3 connects the ring finger end to pinky finger end via the end opposite the thumb end of primary whippletree.
5. Figure 2 shows shows how the whippletrees are connected to the fingers (Strings 1,2, and 3) and the whippletrees to each other (String 4). String 5 connects to the center hole in the Secondary Whippletree and extends to the Tensioner (Tensioner not shown). String 5 needs to be long enough to reach from the secondary whippletree to the bicep areas of the recipient’s arm. It is recommended to attach String 5 later in the assembly process (see Latch Assembly Step 6).

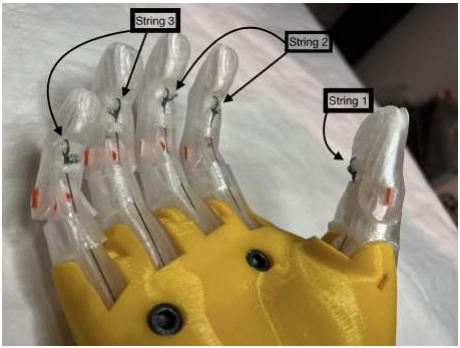
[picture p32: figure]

Figure 1: Stringing the Hand: Fingers

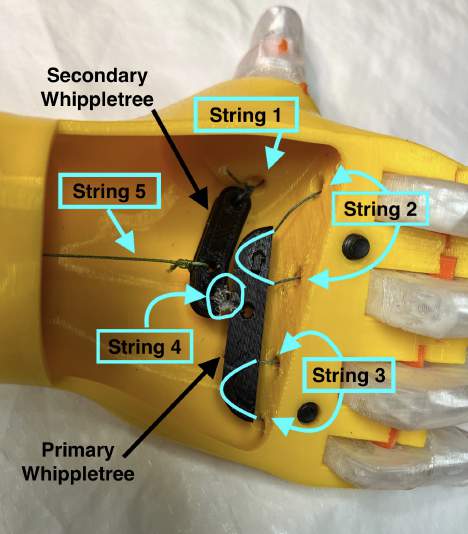
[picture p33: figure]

Figure 2: Stringing the Hand: Palm
6. As shown in Figure 2, with all fingers extended, the the Primary Whippletree should be close to the area in the Palm where Strings 2 and 3 enter the palm area. When the Whippletrees are tied together (String 4) and thumb extended, the thumb side of secondary whippletree should be close to the palm area where String 1 enters the palm. This will give the whippletrees adequate room to move when fingers and thumb are clenched.

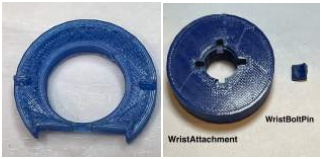
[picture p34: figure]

WristCover

WristBolt | WristButton
Figure 3: Wrist Components
7. Figure 3 shows components in the wrist. To make sure parts will function properly when assembled, first make sure that the WristButton and WristCover will fit over the WristBolt all the way to the WristBolt pedestal and are able to turn freely. The WristCover was designed to be a tight fit, so it may be necessary to grind/file the ID of the WristCover so that it will fit and turn properly. Also the WristBolt must fit into the hole on the palm top and be able to turn freely. Again, the ID of the Palm top hole may have to be expanded by filing/grinding.
8. Test the WristBolt to make sure it threads into the WristAttachment. Filing in the threads of the bolt may be required to initially get the WristBolt fully engage in the WristAttachment threads. The application of a dry lubricant to the threads will help to obtain a smooth turning of the bolt into the WristAttachment. After obtaining smooth threading of the bolt into the socket, remove the WristBolt from the WristAttachment.
9. Place the WristButton into the top of Palm cavity. While pushing the button, insert the WristBolt into Palm cavity and push the threads out of the top opening. Then place the WristCover over WristButton such that the wedge shaped structures will fit into the recesses in the Palm.
10. Thread the WristBolt onto the WristAttachment until it is tight making sure the slots in the WristAttachment are visible. Then loosen the WristAttachment until the first slot in the WristAttachment lines up with the slot in the WristBolt. Insert the WristBoltPin in the slot to lock the WristAttachment to the WristBolt.

Forearm and Cuff Assembly Part 1
1. Arrange the plastic Cuff and Forearm pieces as shown in Figure 4. This figure shows a right arm assembly. The left arm configuration would be the mirror image of this figure.

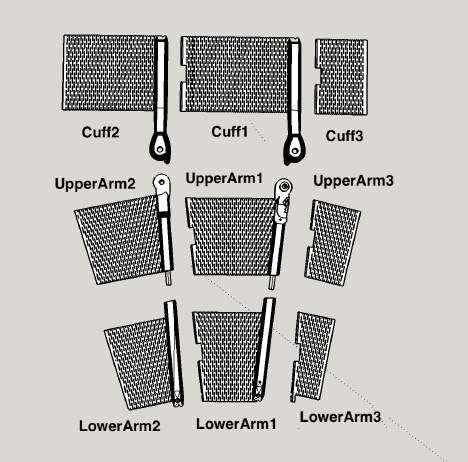
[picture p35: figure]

Figure 4: Forearm and Cuff Part Layout
2. UpperArm1 connects with LowerArm1 and UpperArm2 connects with LowerArm2. However, because the joint may tend to be weak point, reinforcement has been designed into the assembly. Figure 5 shows where 2mm wire is designed to be inserted into these parts to make them significantly stronger. Two wires per joint are required.
3. Figure 5 represents the the joint between the UpperArm and LowerArm. Measure the depth of each hole and cut a 2mm wire to span the distance - do not take into account the alignment peg in measurements. Insert the two wires into holes on one plastic brace -there will be a significant length extending—then insert this end into the corresponding holes in the other arm brace. Slide it all the way including the Alignment peg into the LowerArm. If all fits properly, use 2 part epoxy to permanently just UpperArm to LowerArm braces. Both Arm1 and Arm2 should have the wire inserts. This process applies to the leather option as well exept of course there is no plastic grid to deal with.

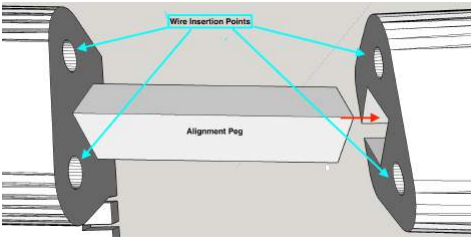
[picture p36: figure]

Figure 5: UpperArm to LowerArm Connection
4. This step applies to the plastic option: Use 2 part epoxy to attach Cuff2 to Cuff1 and Cuff3 to Cuff 1—see orientation in Figure 4.
Similarly, attach UpperArm2 to UpperArm1 and UpperArm3 to UpperArm1.
Likewise, attach LowerArm2 to LowerArm1 and LowerArm3 to LowerArm1.
5. This applies to the Leather Option: Lay the three leather pieces (cut previously) flat with the top smooth surface that will eventually be in the contact with the skin of the recipient. Use Figure 4 to align the leather similar to the layout of the plastic parts and make sure holes align properly. Verify the holes in the cuffs line up with the holes in the leather.
6. Leather Option: Attach the leather to the printed parts using Rivets or Chicago type fasteners. Push the fasteners through the leather and plastic and seal from the plastic side.
D. Latch Assembly
1. Prepare to assemble the latch mechanism—Latch, LatchCover, Ratchet, and Tensioner onto the UpperArm. See Figure 6.

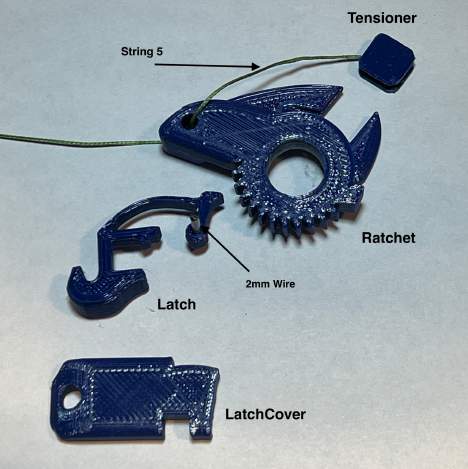
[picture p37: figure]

Figure 6: Latch Mechanism
2. Cut a piece of 2mm wire/hanger to span from the hole in the UpperArm Latch recess, through the Latch and into the hole in the LatchCover. The hole in the Latch may have to be widened to be able to insert the wire—use appropriate sized drill bit if necessary. Insert the wire in the Latch hole to act as an axel in the Latch and set the Latch with wire into the forearm recess.
3. Place the LatchCover over the Latch making sure the wire is inserted in the hole supplied. Use a #4 pan head sheet metal screw to attach the LatchCover to the forearm.
4. With the Latch pulled back (off position), place the Ratchet in place. Make sure the Latch will engage in the Ratchet teeth when in the forward (on) position.

5. Insert the Tensioner in the slot in the side of the Ratchet (see Figure 6). It should fit in all four of the possible orientations. Some trimming of the Tensioner may be required in certain orientations.
6. Push one end of String 5 through the Egress Port in Arm1 (see Figure 7) then thread it into the WristBolt and into the Palm cavity. Attach the string to the center hole of the Secondary Whippletree as shown in Figure 2. This description is applicable to both Leather and Plastic options.

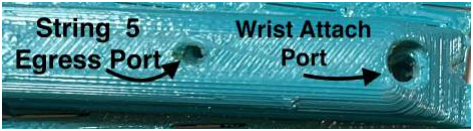
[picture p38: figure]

Figure 7: Lower Arm Brace showing String 5 Egress and Forearm to Wrist Attach
7. Use sheet metal screws to attach the plastic LowerArm braces to the WristAttachment port on the wrist. There are 2 holes in the WristAttachment for this. Use 2 part epoxy to help secure the plastic or leather to the WristAttachment.
8. Cut String 5 such that it extends past the Ratchet on the forearm. Thread the free end of the string up through the hole in the Ratchet as shown in Figure 6, then remove the Tensioner from the Ratchet and tie it to the Tensioner through the center hole in its axel. Super glue both knots in String 5. Wind string 5 around the Tensioner to tighten and reinsert the Tensioner into the Ratchet slot.
9. The PalmCover can now be attached over the palm cavity by fastening it with 2 bolts selected earlier. The Forearm and Hand Assembly is complete.
E. Cuff and Forearm Part 2
1. Using Bolts previously selected, attach Cuff1 to the Ratchet/Latch side of UpperArm1 and attach Cuff2 to the opposite side. It may be helpful to use an appropriate size tap to clean the threads on the UpperArm.
2. Use three velcro straps having the width as chosen initially and thread it through the gaps between the plastic or leather and through the attached loop at the velcro end. The straps will allow the cuff and forearm to be tightened as necessary
3. Flex the cuff and verify finger movement. If String 5 is not tight enough, remove the Tensioner from the Ratchet slot and wind the string tighter and place it back in the Ratchet slot
F. Padding Install
Plastic Cuff:
1. Plastic Cuff and Forearm: Silicone or Neoprene option–Cut three pieces of padding to fit on the inside of the Cuff and Forearm parts. Peel the backing and apply it to the Cuff, UpperArm and LowerArm.
2. Leather Cuff and Forearm– the leather option does not need padding.

G. Final Comments
Optional
1. Plasti Dip is commonly used on fingers and palms to enhance the ability to pick and hold things because it adds tackiness to the plastic fingers. Plasti Dip Primer is recommended prior to painting with the Plasti Dip. The joints and strings in the fingers should not be exposed to Plasti Dip.
2. Lee Tippy Nail’s Gel Finger Tips can be purchased and placed over the ends of the plastic fingers to enhance gripability

Final Testing
1. Exercise the wrist lock mechanism to make sure the hand can be turned 360 degrees and can be locked at any selected location.
2. Exercise the latch mechanism. In the engaged position, the latch should lock the fingers in position depending on the extent of elbow rotation.
3. With the latch in the engaged position, fingers should maintain their clutched position even when the elbow is straightened,

Assembly is complete

Hurray!!!

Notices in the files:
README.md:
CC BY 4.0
